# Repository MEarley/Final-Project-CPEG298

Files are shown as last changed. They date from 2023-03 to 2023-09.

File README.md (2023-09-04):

# Internet of Things Device for a Microbial Fuel Cell: IoT MFC
The purpose of this device is to measure the voltage and the surrounding environment of the said cell for research purposes.

## Schematic of SMART MFC (KiCAD)
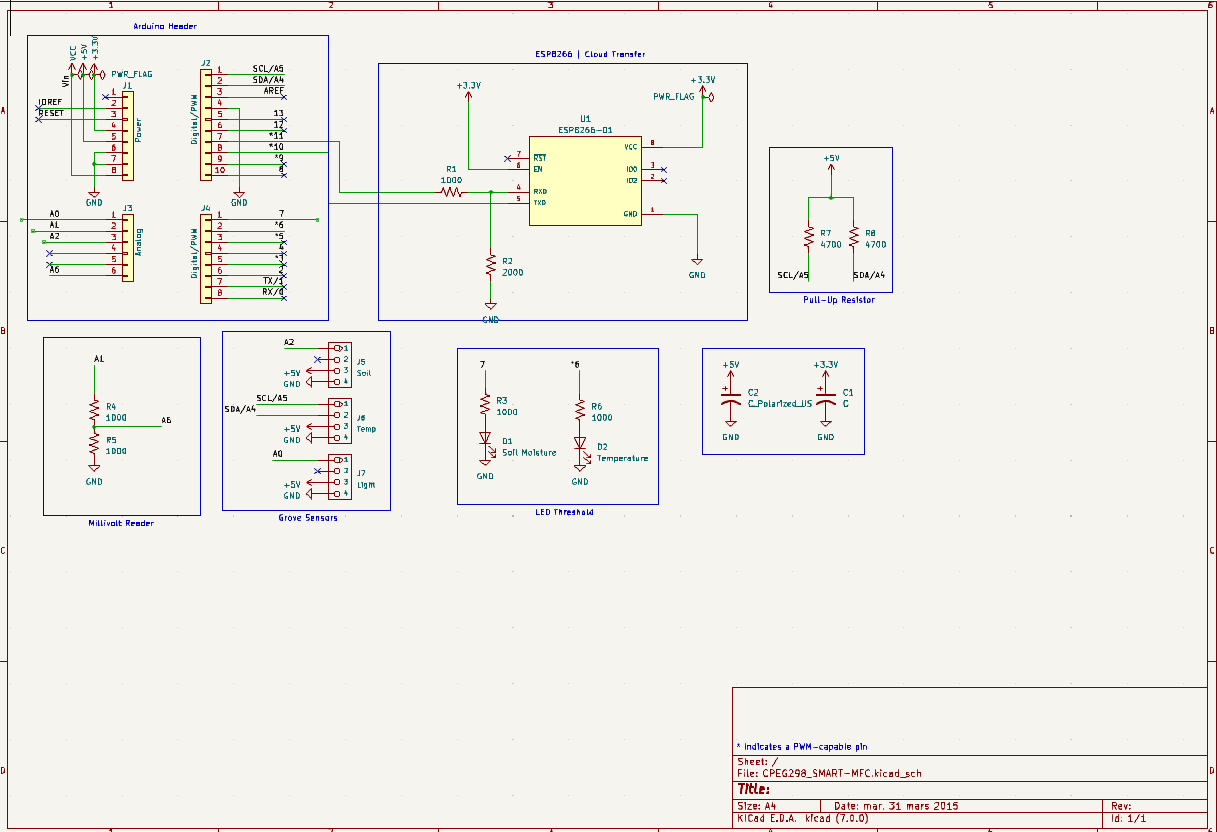
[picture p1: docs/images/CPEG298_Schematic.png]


## SMART MFC CAM
### Front 									
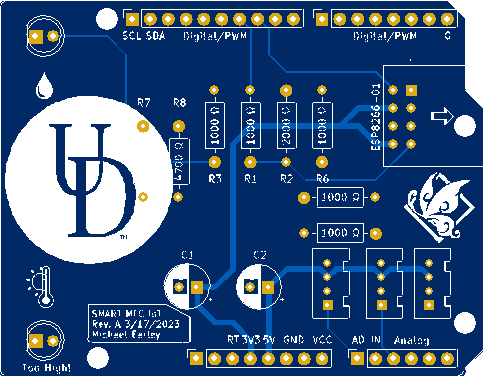
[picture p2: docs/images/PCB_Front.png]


### Back
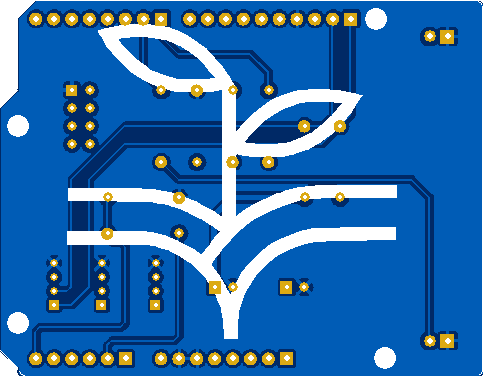
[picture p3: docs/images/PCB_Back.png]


## SMART MFC BOM
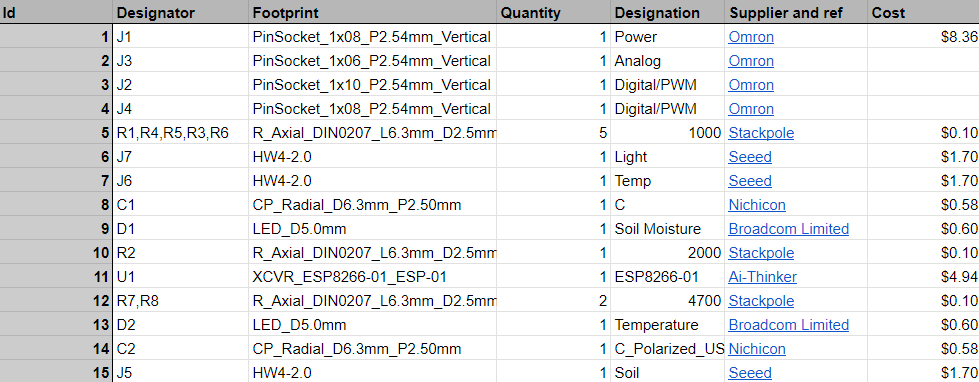
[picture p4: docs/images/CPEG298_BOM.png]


## Arduino code
The entire Arduino sketch is divided into 3 main functions: setup(), loop(), and espData(). 

##### Note: There is also a very minor calculateVoltage() function. However, this is rather self-explanatory. 

The setup() function begins by setting up the serial monitor and the ESP8266 to a baud rate of 9600. Using the ESP8266, it connects to the internet to access Adafruit IO using both usernames and passwords given by the user. After the ESP8266 has successfully connected to Adafruit, analog pins for the light sensor, soil moisture sensor, and voltage reader are set. In addition, the DHT20 is set up using the freely accessible library by Rob Tillaart.

Within the loop() function, the entire block of code repeats every ~5 seconds. This delay is due to the fact that Adafruit only allows a maximum of 30 uploads/minute for free. Using the analogRead() function from the Arduino library, the Arduino Uno collects data in relation to the light, soil moisture, and voltage levels. In addition, the DHT20 library is used to get the humidity and temperature values from the DHT20 sensor. After each reading, the data is transmitted through the ESP8266 to Adafruit where it can be graphically displayed. This loop() function also sets threshold values for the soil moisture level and the temperature values.

Within the espData() function, the given command and data are sent to the ESP8266 using Serial UART. After the data has been sent, the function waits for a response from the ESP8266. This leads to the function printing out the response within the Serial Monitor where it can be viewed for debugging purposes.

## Libraries and Additional Sources
 • Arduino.h
 
 • Wire.h

 • SoftwareSerial.h | Allows usage of two GPIO pins for a second UART

 • DHT20.h | Allows for easier usage of the DHT20
   ESP8266 Example program provided by Theo Fleck and Rick Martin
   DHT20 Demo code provided by library author Rob Tillaart

## Adafruit Dashboard
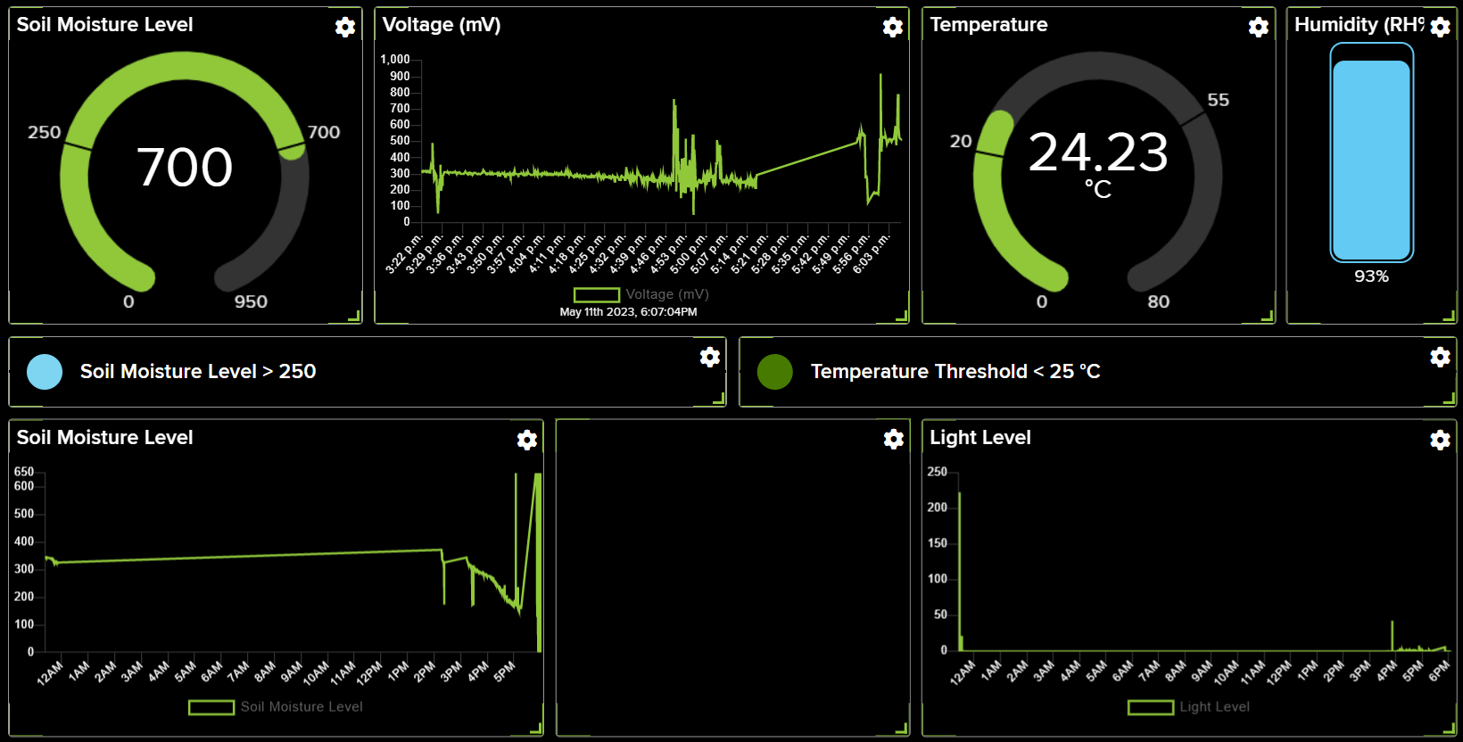
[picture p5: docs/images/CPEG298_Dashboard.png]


### Line Graphs

 • Light Level | Displays the level of light over a given time interval time

 • Soil Moisture Level | Displays the level of moisture in the soil over a given time interval time

 • Voltage | Displays the voltage in millivolts of the MFC in a given time interval time   
### Circle Graphs

 • Soil Moisture Level | Displays the current level of moisture within the soil with thresholds between 250 - 700

 • Temperature | Displays the current temperature with a threshold between 20 - 55℃
### Indicators

 • Soil Moisture Level | Indicates when the current soil moisture level is over 250

•  Temperature Level | Indicates when the current temperature is below 25℃

•  Humidity Bar Graph | Displays current relative humidity

•  Feed | Displays data messages between Adafruit and the ESP8266

## Future Changes
In terms of redesign, the voltmeter on the reader still requires tweaking and is the only leading cause of concern. Its purpose in this project is to measure the produced voltage from a Microbial Fuel Cell, which in itself is like a battery having both a positive and negative node. The rise of concern comes from trying to read the amount of voltage produced by the said battery. The Microbial Fuel Cells, or MFC, that are being used in this report can range from 1 mV to 100 mV or more. 

At first, I attempted to read the voltage directly using analogRead(). However, the voltage could not be read due to the voltage being too small. After further research, I came to the conclusion of two possible solutions. 

Solution #1 is an op-amp with a high gain. However, with a capped supply voltage of 5V and a high range of 1-100+ mV, deciding an appropriate gain may be tricky. This would also require additional wiring and spacing for the PCB layout. 

While Solution #1 has a more hardware approach, Solution #2 approaches the problem through the software and proved to be more successful to an extent. Solution #2 is what is seen in the current design: the calculateVoltage() function. This function changes the reference voltage from the default 5V to 1,1V. This allows me to measure the number of millivolts directly from the MFC. While experimenting with a standalone program and an empty Arduino board, this solution works fine. However, in practice, there are further complications. After connecting the MFC’s positive voltage to its corresponding analog pin and its negative terminal to GND, the introduction of this power source causes interference within the other sensors: most notably, the soil moisture sensor. Both the soil moisture sensor and voltmeter begin producing the wrong results at an extreme degree. My assumption is that the amount of noise generated in GND by the other components on the board is too much for the millivolts reader. To improve this design, I would first need to learn how to reduce/diminish the cause of this disruption.

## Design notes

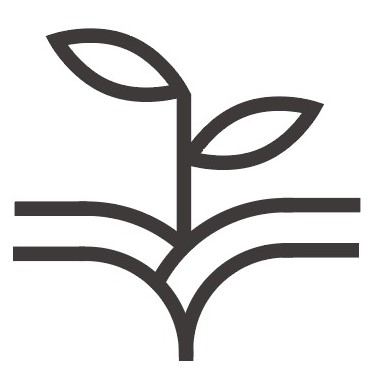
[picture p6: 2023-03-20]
docs/images/Sprout.jpg

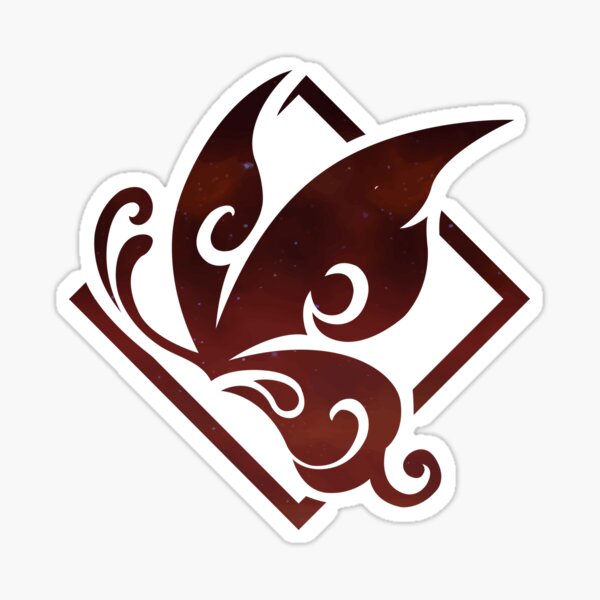
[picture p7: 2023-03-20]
docs/images/ButterFly.jpg

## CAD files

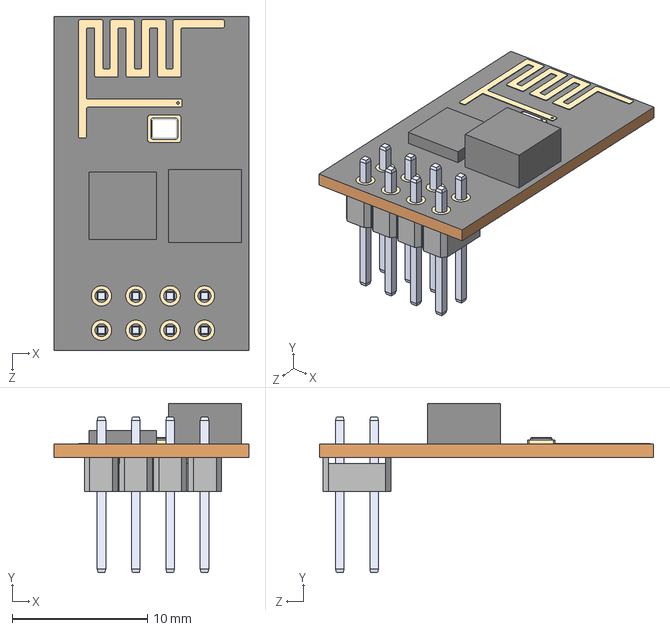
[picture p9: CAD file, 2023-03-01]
ESP8266-01_ESP-01/ESP8266-01_ESP-01.step
14.4 x 12.5 x 24.7 mm

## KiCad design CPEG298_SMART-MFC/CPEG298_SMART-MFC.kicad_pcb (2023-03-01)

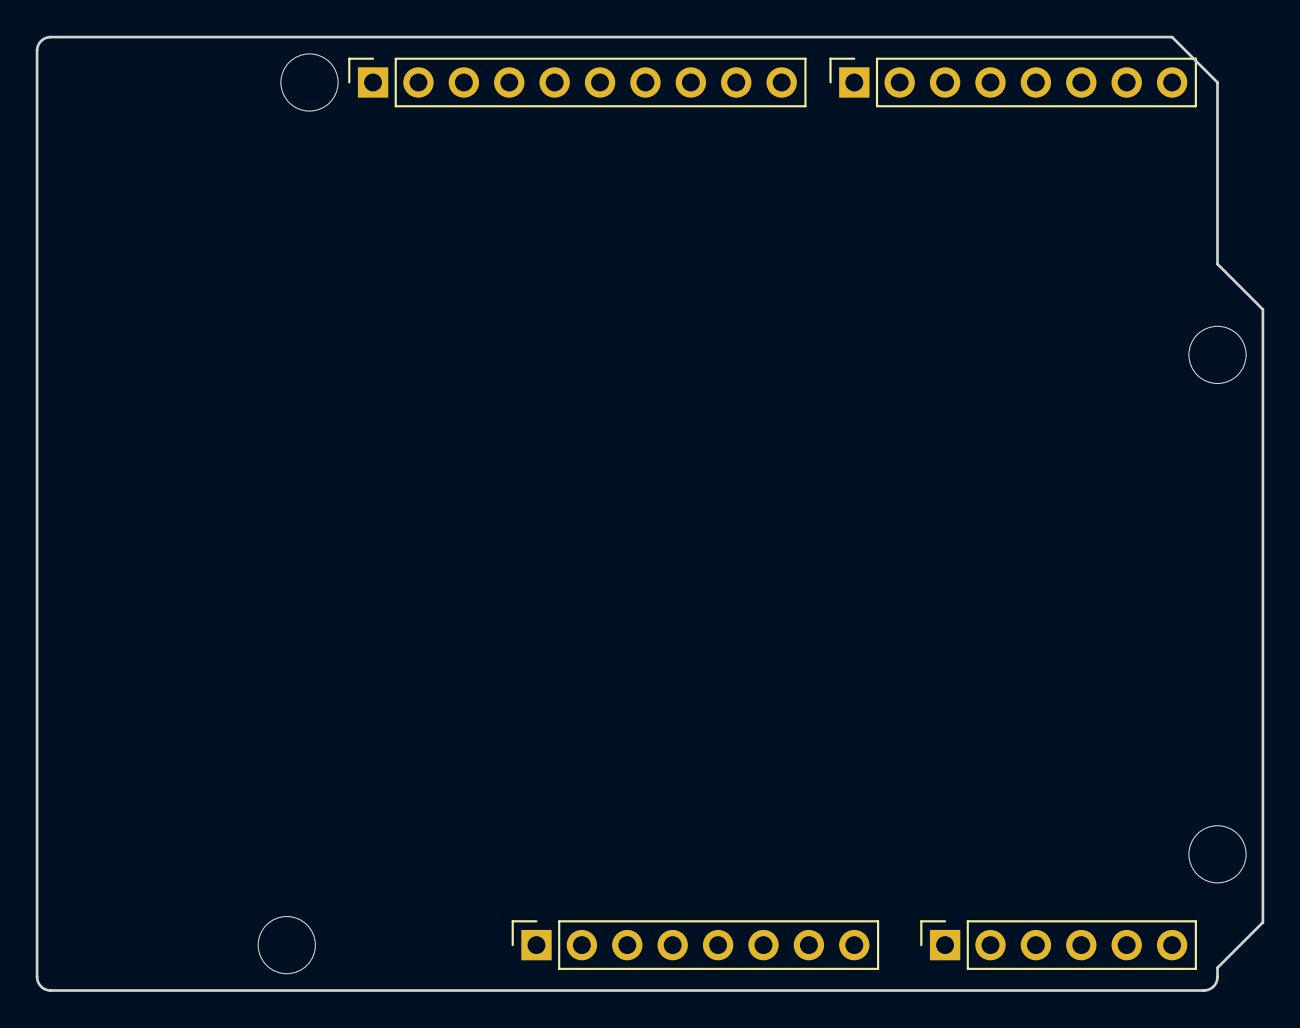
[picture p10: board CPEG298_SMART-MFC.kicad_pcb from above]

Board: 2 copper layers, 68.6 x 53.3 mm, 8 parts (0 on the bottom side), 3 nets, no tracks yet.

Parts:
J1: Power; PinSocket_1x08_P2.54mm_Vertical
J2: Digital/PWM; PinSocket_1x10_P2.54mm_Vertical
J3: Analog; PinSocket_1x06_P2.54mm_Vertical
J4: Digital/PWM; PinSocket_1x08_P2.54mm_Vertical
MH1, MH2, MH3, MH4: MountingHole_3.2mm

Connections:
/SCL/A5: J2.1, J3.6
/SDA/A4: J2.2, J3.5
GND: J1.6, J1.7, J2.4

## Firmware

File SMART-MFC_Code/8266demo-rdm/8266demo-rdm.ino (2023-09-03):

/***************************************************************************
  SMART MFC
    IoT Device code for a Microbial Fuel Cell: MFC for short. The purpose of this
    device is to measure the voltage and the surrounding environment
    of said cell for research purposes.
    Measures:
      Millivolts, Temperature, Humidity, Light, and Soil moisture 

  written by Michael Earley
  05/8/2023
 ***************************************************************************/
#include "Arduino.h"
#include <SoftwareSerial.h>		          //Allows us to use two GPIO pins for a second UART
#include <Wire.h>
#include <DHT20.h>                      // Library used to access the DHT20 (By Rob Tillaart)
DHT20 DHT(&Wire);

#define TEMPPIN D3
#define TEMPTHRESHOLD 25
#define TEXTDIVIDER "__________________________________________"

SoftwareSerial espSerial(10,11);	      //Create software UART to talk to the ESP8266

String IO_USERNAME = "";		    // Adafruit IO used
String IO_KEY  =     "";
String WIFI_SSID = ""; 	    
String WIFI_PASS = ""; 		            //Blank for open network

float temperature;
int lightLevel;
float humidity;
float voltage = 0.000000000;

float moisture;
const float VOLTREF = 1.1;

// Define Pins
const int LIGHTPIN = A0;
const int VOLTPIN = A1;
const int SOILPIN = A2;

/***************************************************************************
  This is an example program for sending a counter to Adafruit IO using
  an ESP8266 WiFi module.  You will need to correct the WiFi SSID and password
  and add your Adafruit IO username and Key.

  written by Theo Fleck and Rick Martin
  03/25/2020
 ***************************************************************************/

void setup() {
	Serial.begin(9600);		// set up Serial monitor with 9600 baud rate
	espSerial.begin(9600);		// set up software UART to ESP8266 @ 9600 baud rate
	Serial.println("setting up");
	String resp = espData("get_macaddr",2000,true);	//get MAC address of 8266
	resp = espData("wifi_ssid="+WIFI_SSID,2000,true);	//send Wi-Fi SSID to connect to
	resp = espData("wifi_pass="+WIFI_PASS,2000,true);	//send password for Wi-Fi network
	resp = espData("io_user="+IO_USERNAME,2000,true);	//send Adafruit IO info
	resp = espData("io_key="+IO_KEY,2000,true);
	resp = espData("setup_io",15000,true);			//setup the IoT connection
	if(resp.indexOf("connected") < 0) {
		Serial.println("\nAdafruit IO Connection Failed");
		while(1);
	}


  // DHT20 Library Setup
  #if defined(ESP8266) || defined(ESP32)
  DHT.begin(12, 13); //  select your pin numbers here
  #else
  DHT.begin();
  #endif

  Serial.print("DHT20 LIBRARY VERSION: ");
  Serial.println(DHT20_LIB_VERSION);
  Serial.println();

  // Sets Pins for Senors
  pinMode(LIGHTPIN, INPUT);
  Serial.print("Light Sensor Pin set to: ");
  Serial.println(LIGHTPIN);
  lightLevel = analogRead(LIGHTPIN);
  pinMode(VOLTPIN, INPUT);
  Serial.print("Voltage Pin set to: ");
  Serial.println(VOLTPIN);
  pinMode(SOILPIN,INPUT);
  Serial.print("Soil Moisture Sensor Pin set to: ");
  Serial.println(SOILPIN);
  moisture = analogRead(SOILPIN);  

  //start the data feed  
  resp = espData("setup_feed=1,Voltage (mV)",2000,false);	// Voltage
  resp = espData("setup_feed=2,Light Level",2000,false); // Light
  resp = espData("setup_feed=3,Temperature (C)",2000,false); // Temperature
  resp = espData("setup_feed=4,Humidity (P)",2000,false); // Humidity
  resp = espData("setup_feed=5,Soil Moisture Level",2000,false); // Soil
  

  // Temp Threshold LED
  pinMode(6, OUTPUT);
  // Moisture Threshold LED
  pinMode(7, OUTPUT);

  Serial.println("------ Setup Complete ----------");
}

// DISCLAIMER: Possibly due to the amount of noise generated in the GND by other components, the millivolt reader does not read the correct values. 
// More tweaking is needed
//returns Voltage in millivolts
void calculateVoltage(void){
  analogReference(INTERNAL);  // Sets voltage reference to 1.1v to allow precise millivolt reading 
  voltage = VOLTREF * analogRead(VOLTPIN);
  Serial.println(voltage);
  analogReference(DEFAULT);  
  delay(1000);
  return;
}

void loop() {

	// free version of Adafruit IO only allows 30 uploads/minute, it discards everything else
  delay(5000);	 // Wait 5 seconds  between uploads	
  // Voltage Meter
  Serial.println(TEXTDIVIDER); // Serial Monitor Divider
  Serial.print("Voltage (mV), ");
  calculateVoltage();
  String resp = espData("send_data=1,"+String(voltage),2000,false); //send feed to cloud
  
  // Reading Grove Light Sensor
  Serial.println(TEXTDIVIDER); // Serial Monitor Divider
  Serial.print("Light Level, ");
  lightLevel = analogRead(LIGHTPIN);  
  Serial.print(lightLevel);
  resp = espData("send_data=2,"+String(lightLevel),2000,false); //send feed to cloud
  
  // Reading DHT20 Grove Temperature sensor
  //-------------------------------------------------------------
  // DHT20 Temperature and Humidity Sensor Demo code
  // By library author: Rob Tillaart
  // Edited by: Michael Earley  

  //  READ DATA
  Serial.println(TEXTDIVIDER); // Serial Monitor Divider
  Serial.print("DHT20, \t");
  int status = DHT.read();
  switch (status)
  {
  case DHT20_OK:
    Serial.print("OK,\t");
    break;
  case DHT20_ERROR_CHECKSUM:
    Serial.print("Checksum error,\t");
    break;
  case DHT20_ERROR_CONNECT:
    Serial.print("Connect error,\t");
    break;
  case DHT20_MISSING_BYTES:
    Serial.print("Missing bytes,\t");
    break;
  case DHT20_ERROR_BYTES_ALL_ZERO:
    Serial.print("All bytes read zero");
    break;
  case DHT20_ERROR_READ_TIMEOUT:
    Serial.print("Read time out");
    break;
  case DHT20_ERROR_LASTREAD:
    Serial.print("Error read too fast");
    break;
  default:
    Serial.print("Unknown error,\t");
    break;
  }

  //  DISPLAY DATA, sensor has only one decimal.
  humidity = DHT.getHumidity();    
  Serial.print(humidity, 1);
  Serial.print("%,\t");
  temperature = DHT.getTemperature();
  Serial.print(temperature, 1);
  Serial.println(" °C");

  //-------------------------------------------------------------

  resp = espData("send_data=3,"+String(temperature),2000,false); //send feed to cloud
  resp = espData("send_data=4,"+String(humidity),2000,false); //send feed to cloud

  // Reading Grove Soil Moisture Sensor
  Serial.println(TEXTDIVIDER); // Serial Monitor Divider
  Serial.print("Soil Moisture, ");
  moisture = analogRead(SOILPIN);
  Serial.println(moisture);
  resp = espData("send_data=5,"+String(moisture),2000,false); //send feed to cloud

  // Soil Moisture Metrics

  if(moisture<=300){
    Serial.println("The soil is dry.");
  }
  else if(moisture > 300 && moisture <= 700){
    Serial.println("The soil is humid.");
  }
  else if(moisture > 700 && moisture <= 950){
    Serial.println("The soil is wet.");
  }
  else{
    Serial.println("ERROR: Undefined Soil Moisture Level");
  }


  // Threshold for Temperature
  Serial.println(TEXTDIVIDER); // Serial Monitor Divider
  if(temperature > TEMPTHRESHOLD){
    digitalWrite(6, HIGH);   
    Serial.print("Temperature exceeds set threshold of ");
    Serial.print(TEMPTHRESHOLD);
    Serial.println(" °C");      
  } else{ digitalWrite(6, LOW); }

  // Threshold for moisture
  if(moisture > 250 /* Place Holder*/){
    digitalWrite(7,HIGH);
  } else{ digitalWrite(7,LOW);}

}

String espData(String command, const int timeout, boolean debug) {
	String response = "";
	espSerial.println(command);	//send data to ESP8266 using Serial UART
	long int time = millis();
	while ( (time + timeout) > millis()) {	//wait the timeout period sent with the command
		while (espSerial.available()) {	//look for response from ESP8266
			char c = espSerial.read();
			response += c;
			Serial.print(c);	//print response on Serial monitor
		}
	}
	if (debug) {
		Serial.println("Resp: "+response);
	}
	response.trim();
	return response;
}

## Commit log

2023-03-01 KiCad Schematic from Template
    -Starting of project
    * Uses Arduino Uno Shield Template
    [CPEG298_SMART-MFC.kicad_pcb, CPEG298_SMART-MFC.kicad_sch]
2023-03-01 PCB and Schematic Updates
    -Added ESP8266-01_ESP-01 Library from snapeda
    -Added ESP8266-01_ESP-01 to schematic
    -Added capacitor bypass
    -Added ground plate to PCB (Back Copper)
    [ESP8266-01_ESP-01.step]
2023-03-02 Updated
    -Trying to fix temp sensor
2023-03-09 Lab5
    -Added Grove Connectors
    -Rewiring
    -3D STEP Files
    -New Libraries
    *SEEED, Digikey
    [CPEG298_SMART-MFC.kicad_pcb, CPEG298_SMART-MFC.kicad_sch]
2023-03-15 KiCad Components and Software
    [CPEG298_SMART-MFC.kicad_sch]
2023-03-15 KiCad & Code
    -Labeling on PCB
    -Preparing code for millivolt reader
    [CPEG298_SMART-MFC.kicad_sch]
2023-03-20 Submission for Review
    [CPEG298_SMART-MFC.kicad_sch]
